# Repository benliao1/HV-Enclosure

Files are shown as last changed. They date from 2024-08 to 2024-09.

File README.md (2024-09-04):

# High Voltage Enclosure

This git repository contains all of the design files (both mechanical and electrical) as well as extensive documentation for the high voltage safety enclosure. It is meant to be living and not used simply as a reference. Any updates to the design should be uploaded to the repository, along with any necessary updates to the documentation files. Keeping these files up-to-date is important, especially since new high voltage enclosures or maintenance / part replacement on existing enclosures may require the files to be used again at any given time (unlike former research projects, which will be used as references but more likely than not will never be built again).

Note: **Do NOT** make a new commit to this repository while Solidworks is open!! Solidworks creates a bunch of temporary journal files and mod files while it is open which should not be committed to the repository.

## Overview

The high voltage safety enclosure is an assembly designed to protect someone in the event of a catastrophic mechanical failure of a converter under test or improper use of electrical equipment during a test which would otherwise result in the possibility of the person touching something at high voltage. The enclosure consists of the following parts:

- A **cover** which can be lowered to cover a portion of the lab bench and raised to allow access to the test setup
- A **latching mechanism** which holds the cover in the raised position
- A **button assembly** which detects when the cover is open or closed and which drives the electrical components of the enclosure
- An **HV Electrical Box** which contains electronics to operate the high voltage contactors and bleeder resistors on the input side of the converter under test
- An **Auxiliary HV Electrical Box** which is an __optional__ assembly containing electronics to operate bleeder resistors on the output side of the converter under test

The cover protects a person against catastrophic mechanical failure and against unintentional contact between a foreign object and the converter under test. The electrical boxes and button assembly ensure that the converter under test can only be energized (i.e. connected to the power supply) when the cover is down; when the cover is up, bleeder resistors are automatically connected across the input to bleed any large input capacitors that may be energized (and, if the auxiliary HV Electrical Box is used, bleeder resistors are automatically connected across the output to bleed any large output capacitors as well).

## Repository Structure

The following is a guide to where various files and components are located in this repository.

- The **mechanical** folder contains all of the CAD models of nearly every component used in the mechanical portion of the HV enclosure. Since the enclosure was designed in Solidworks, all CAD files are `.sldprt`, `.sldasm`, or `.step` files. Notably, this folder does **not include** any bolts, nuts, or L brackets used in the cover, and does **not include** the gate latch used in the latching mechanism. Below is a list of the kinds of files that can be found here:
	- All 8020 beams used in the cover and electrical boxes
	- All acrylic pieces used in the cover and electrical boxes
	- 3D exported renderings of the various PCBs in the design
- The **electrical** folder contains all of the Altium component libraries, schematics, and layouts for the various PCBs designed for the HV enclosure. Below is a list of the PCBs used in the design:
	- **Main Board**: this board connects to the incoming 12 V DC supply from the wall, sends power to the other boards, operates the contactors, sends signals to operate the bleeder resistors, receives the signal from the button detecting when the cover is closed or not, and displays the state of the system to the user.
	- **HV Board**: this board connects the power supply and the converter under test. It contains the high-voltage JFETs that connect/disconnect the bleeder resistors across the input of the converter, as well as mounting holes for the contactors which electrically connect/disconnet the power supply from the converter under test.
	- **Auxiliary HV Board**: this board connects the converter under test with the load. It contains high-voltage JFETs that connect/disconnect the bleeder resistors across the output of the converter.
	- **Button Board**: this board houses the lever switch which detects when the cover is closed, which is sent to the Main Board.
- The **production** folder contains all of the files that will be uploaded to various supplier websites for custom fabrication:
	- The `.STL` file of the button board holder model
	- The `.DXF` files for all of the acrylic panels
	- The `.DXF` files for all of the aluminum heat sinks
	- The `.ZIP` files containing the gerbers for all of the PCBs
- The **docs** folder contains more documentation and useful reference material:
	- BOMs for the mechanical and electrical components used in the HV enclosure (as well as the suppliers and supplier links of those components)
	- What supplier manufacturing options were selected when ordering the parts for the HV enclosure
	- Assembly instructions for the HV enclosure
	- Documents describing what needed to be considered and what principles were followed throughout the design process
	- All photos and screenshots used in the repository

## Quick Specifications

The following is a list of the most important specifications of the system as designed in the first prototype:

- Rated voltage: 1000 V
- Rated current (banana plugs): 25 A per plug
- Rated current (Phoenix connector): 75 A per pin
- Bleeder resistor value: 4x 390 Ohms in parallel (total 97.5 Ohms)
- Bleeder resistor power ratings: 100 W per resistor (continuous, with heat sink); 12.5x overload for 2 seconds
	- Maximum power dissipation is 5 kW for 2 seconds across entire resistor bank - appoximately enough to discharge 10 mF of input capacitance at 1000 V, reducing the voltage on the input bus below 100 V in a little over 2 seconds (see [datasheet](https://www.te.com/commerce/DocumentDelivery/DDEController?Action=srchrtrv&DocNm=1773035&DocType=DS&DocLang=English), page 3 "Power Overload" graph for details)

## Credits

First prototype designed and assembled by Ben Liao in late 2023 to mid 2024 (completed August 2024). Contributors to this first iteration included Logan Horowitz, Nathan Biesterfeld, Nathan Miles Ellis, and Robert Pilawa. Original documentation written by Ben Liao.

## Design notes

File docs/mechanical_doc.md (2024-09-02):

# Mechanical Design Documentation

This document contains information on the design process for the mechanical portion of the enclosure, notes on working on and editing the files/design, and the parameters that can be changed (for example, to make the box wider or narrower).

## Structure of `mechanical` Folder

To access the assembly, it is recommended to start by opening the `mechanical/full_model.SLDASM` file. Right clicking on indivisual components and selecting "Open Part" or "Open Subassembly" allows you to open additional components in the assembly. If you want to open individual components directly, the structure of the `mechanical` folder is as follows:

- `mechanical`: root directory
	- `full_model.SLDASM`: complete model of the enclosure along with desk and instruments for comparison. The cover can be moved up and down in this model by clicking and dragging it up and down.
	- `desk_and_instrument_models`: models of the desk, shelves, large DC power supply, large electronic load, and typical oscilloscope used in the full model.
	- `subassemblies`: various subassembly files that together make up the full model. This includes the cover and the electronics (which itself is made up of multiple subassemblies)
	- `parts`: all of the `.SLDPRT` files that makes up the enclosure.
		- `2020`: Solidworks part models of 20 series aluminum profile beams from [8020.net](8020.net) of various sizes, along with a drawing of the cross section and a base model (which can be copied and modified to create additional beam lengths should they be needed).
		- `acrylic`: Solidworks part models of all the acrylic pieces used in the cover and both the HV Electrical Box and the Auxiliary HV Electrical Box.
		- `bleed_resistor_parts`: Solidworks part models of the various components used to hold the bleed resistors and their aluminum heat sinks to the electrical boxes. This includes the nylon spacers and large L brackets.
		- `contactor_parts`: Solidworks part models of the contactor and the electrical connector used to operate the contactor coil
		- `miscellaneous`: Solidworks part models of miscellaneous components mainly used to connect other components together:
			- Standoffs for holding the PCBs inside the high voltage electrical boxes
			- The handle on the cover
			- The bar attached to the cover which engages with the gate latch on the top shelf (the gate latch is not modeled here, only the bar)
			- The 3D-printed holder for the button board which allows the button board to be precisely placed to detect when the cover is closed

## Design Considerations

This section describes the functional considerations that were taken into account throughout the design process.

- **Weight**: the cover and high voltage electrical boxes cannot be too heavy, since that would put undue stress on the mounting screws attached to the hinge attachment assemblies, especially when the cover is in the raised position
- **Cost**: highly specialized parts were mostly avoided, and the amount of structural material kept to a minimum in an effort to reduce cost
- **Ease of Use**: Spaces were left between the top of the cover and the front of the first shelf above the lab bench, as well as between the side panels of the cover and the lab bench, so that the user can route oscilloscope probes and control wires easily. The high voltage electrical boxes were also fitted with a simple connection to the 120 V AC grid for power, which eliminates the need for attaching a separate power supply to the enclosure.
- **Stability**: The cover is designed to be stable in the raised position; i.e. the cover will stay in the raised position by resting against the top shelf. The gate latch is not needed to keep it in the top position, but for greater safety and insurance that the cover won't fall down unexpetedly, it's still advised to latch the cover whenever it is in the raised position
- **Electrical Insulation**: Since there will be high voltage and current flowing through the high voltage electrical boxes, is is undesirable to openly expose the conducting surfaces of the high voltage boards and bleed resistors. The electrical boxes were designed to enclose the high voltage boards on five sides (with the underside of the first shelf forming the sixth side), protecting them from foreign objects as well as confining the high voltage to that small volume. In the event that a wire inside the box somehow breaks loose, the wire will not touch a piece of metal and energize the cover itself (unless it accidentally touches the tips of one of the bolts holding the acrylic to the metal box structure).

## Creating New 20 Series Profile Lengths

To makes a new 20 series beam length in Solidworks, go to `mechanical/parts/2020` and open `2020_base.SLDPRT`. Click on the Boss Extrude feature and edit the extrusion length as desired. Save the edited part as a new file and name it following the naming convention: `2020_<length>` where the length is in cm. For example, `2020_100` is 100 cm long. Lengths with decimals have dashes in replace of the period, e.g. `2020_25-4` for a beam 25.4 cm long.

## Nylon Spacers

Nylon spacers were used to separate the heat sinks and the acrylic panels because nylon has a higher melting temperature than acrylic and also resists thermal deformation below the melting temperature. Thus, in the event the bleed resistors and their heat sinks get extremely hot in an extreme use case, the nylon spacers will hopefully prevent the heat sinks from heating up the acrylic panels so much that they deform or otherwise cause structural damage to the high voltage electrical boxes.

## Allowable Dimension Adjustments

The height of the enclosure cannot be easily changed as the angle the cover makes with the lab bench is set; changing the height of the enclosure (i.e. the distance between the first shelf and the lab bench) would require changes to both the height and width of the cover as well as the non-right angle in the acrylic cover side panel.

### Enclosure Width

To change the width of the enclosure, the following items need to be edited:

- The length of the 20 series beams at the top and bottom of the cover
- The width of the acrylic top panel of the cover
- The length of the 20 series beam holding up the high voltage electrical boxes

All of these should be modified by the same length.

### Length Enclosure Extends Underneath First Shelf

If the supports for the enclosure interfere with the placement of lights underneath the first shelf, the following can be shortened to make room:

- The length of the 20 series beam in the hinge assemblies holding the enclosure to the bottom of the shelf

It is probably best to leave this beam to be as long as possible, as a longer beam provides better support. To make this distance even shorter, it may be necessary to modify the dimensions of the high voltage electrical boxes or turn them 90 degrees to mount them lengthwise along the aluminum bar.

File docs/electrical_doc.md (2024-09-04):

# Electrical Design Documentation

This document contains information on the design process for the electrical portion of the enclosure, notes on working on and editing the files/design, and the parameters that can be changed.

**It should be noted that much of the electronics is actually explained in the Altium schematics. Please read those for very detailed explanations of how the electrical circuitry actually works.** Thus, there will not be any documentation in this document explaining how the boards works.

## Structure of `electrical` Folder

The structure of this folder should be relatively self-exlanatory. Each of the four PCBs has its own Altium PCB Project, containing a schematic file, a layout file, and (with the exception of the Button Board) a populated smart BOM file for convenience. The two integrated libraries `HV_Box_IntLib.IntLib` and `Load_Bank_New_IntLib.IntLib` need to both be installed into your Altium workspace to properly open the files. Apologies for the fact that there's two integrated libraries -- I (Ben) didn't really know how they worked when I started this project so I used both a new integrated library created just for this project as well as components from a previous project I did.

## Schematic Rules and Net Classes

The schematics were made very carefully with a mind towards ease of understanding, good organization, and self-documentation. Generally, logic and power flow from left to right, top to bottom. Each section is demarcated with thick dark red boxes, and with a comment explaining the purpose and various quirks (if any) of that particular section.

Since all the PCBs (except the Button Board) have sections which handle different power regimes that require different clearances in the layout, each net on the boards is assigned a net class:

- "Low Voltage": this net class contains all logic signals and power rails that are referenced to the ground of the 120V-12V AC/DC converter plugged into the wall. The maximum voltage on any of these traces is 12 V.
- "Isolated": this net class contains all logic signals and power rails that have passed through either isolated gate drivers or the isolated power converts, but **do not** directly handle the high voltages and currents associated with the converter under test. The ground reference of these traces is the `JFET_SOURCE` net, i.e. the voltage attached to the source of the JFETs which connect/disconnect the bleeder resistors. The maximum voltage of any of these traces relative to that reference is 12 V, but the isolation barrier can see up to the voltage rating of the enclosure (1 kV), requiring large clearances between this net class and the Low Voltage net class.
- "High Voltage": this net class contains all of the mounting points, copper pours, and jacks which handle the high voltage and current associated with the converter under test. Every net in this net class can see a voltage difference of up to the voltage rating of the enclosure with every other net in the class, so all nets in this class requires large clearances with other members of the High Voltage class, as well as all members of the Isolated and Low Voltage classes

The three net classes are also assigned colors to make them easy to identify in both the schematic and the layout:

- "Low Voltage" class nets and blankets are colored yellow yellow
- "Isolated" class nets and blankets are colored blue blue
- "High Voltage" class nets and blankets are colored red red

## Connecting to the HV Board/Aux HV Board Phoenix Connectors

The Phoenix connectors that will connect to the ones used on the HV Board and Aux HV Board is the one at [this Digikey link](https://www.digikey.com/en/products/detail/phoenix-contact/1969373/2526720).

## Connecting Additional Current

The current rating of the contactors is 150 A. The banana blugs are rated for 25 A each, and the Phoenix connector is rated for 76 A. Here are the different ways to connect to the board for different current regimes:

- 0 A - 25 A: One set of banana plugs OR the Phoenix connector
- 25 A - 50 A: Both sets of banana blugs OR the Phoenix connector
- 50 A - 76 A: Phoenix connector
- 76 A - 101 A: One set of banana plugs AND the Phoenix connector
- 101 A - 126 A: Both sets of banana plugs AND the Phoenix connector
- 126 A - 150 A: Both sets of banana plugs AND the Phoenix connector AND a thick wire screwed directly to the M6 bolt connected to the contactor terminals

For current greater than 150 A, you will need to replace the contactor with one that can break higher current. Luckily, the manufacturer of the contactor used in the prototype makes contactors with higher rated currents in the same form factor, so that should be a quick swap-in if desired. However, the PCBs were only designed to handle 150 A, so pushing the PCBs past 150 A could result in some overheating in the copper pours.

## Contactors vs. Solid State Breakers

When designing the enclosure, there was a long discussion about whether to use contactors or solid state breakers to break the current between the supply and the converter under test. Solid state breakers are, in theory, better than contactors since they can turn on and off much faster and are cheaper / less bulky than contactors. But, in reality, there are no solid state breakers than can simultaneously block 1 kV and pass 150 A of current; you can only get one or the other. As such, there would need to be two different versions of the enclosure: one for high voltage, low current; and another for low(er) voltage, high current. This has the potential to cause a lot of confusion for the user. Additionally, the on-state resistance of solid-state breakers is typically greater than contactors, and at sufficiently high currents, would need heat sinks and a cooling apparatus to maintain safe operation. These would add a lot of bulk to the high voltage electrical box (comparable to the contactor) and a lot of additional complexity. The final reason that contactors were chosen over solid state breakers was that there was a concern that the contactors would wear out quickly because contactors have a relatively low life if they are constantly breaking high current (i.e. turning off at high current). This is true, but the only time that the contactors in the high voltage enclosure need to turn off at high current is if the user lifts the cover while a test is running (and thus, current is flowing through the contactor from the supply to the converter under test). Presumably, this should happen exceedingly rarely; under normal operation, the contactor stays closed for the entire duration that the system is energized. Thus, the relatively low life of the contactors when subjected to repeated high-curent breaks is of little concern to us.

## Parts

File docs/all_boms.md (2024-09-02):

# All BOMs

This document contains Bills of Materials for the entire enclosure, organized in two different ways. The first section is a list of components needed to build each section of the enclosure (PCBs, Cover, High Voltage Electrical Box, Auxiliary High Voltage Electrical Box, Wiring). The second section is all of the components needed to build the entire enclosure organized by supplier (JLCPCB, OSH Stencil, Digikey, 8020.net, Xometry, Sendcutsend, McMaster-Carr, a home improvement or electronics store, and Amazon).

# Section One (By Enclosure Section)

## PCBs

These BOMs contain the components needed to build **one** of the specified PCB with no attachments. They are duplicated in the Altium Smart BOMs. They do not include components that are not modeled in Altium, such as the contactors, bleeder resistors, and JST connector wires. See the BOMs for the [High Voltage Electrical Box and Auxiliary High Voltage Electrical Box](#electrical_box_boms) for those line entries.

### Button Board

| Part Name              | Quantity | Digikey Link                                                                                       |
|------------------------|----------|----------------------------------------------------------------------------------------------------|
| JST 3-pin connector    | 1        | [here](https://www.digikey.com/en/products/detail/jst-sales-america-inc/B3B-PH-SM4-TB/926642)      |
| Res. 100k 0.5%         | 1        | [here](https://www.digikey.com/en/products/detail/yageo/RC0603DR-07100KL/5917788)                  |
| Lever switch           | 1        | [here](https://www.digikey.com/en/products/detail/omron-electronics-inc-emc-div/D2FS-FL-N/4753388) |

### Main Board

| Part Name                        | Quantity | Digikey Link                                                                                                                                                                                                                                                                                                                                                                                                              |
|----------------------------------|----------|---------------------------------------------------------------------------------------------------------------------------------------------------------------------------------------------------------------------------------------------------------------------------------------------------------------------------------------------------------------------------------------------------------------------------|
| JST 2-pin connector              | 2        | [here](https://www.digikey.com/en/products/detail/jst-sales-america-inc/B2B-PH-SM4-TB/926641)                                                                                                                                                                                                                                                                                                                             |
| JST 3-pin connector              | 3        | [here](https://www.digikey.com/en/products/detail/jst-sales-america-inc/B3B-PH-SM4-TB/926642)                                                                                                                                                                                                                                                                                                                             |
| Phoenix connector 2x1 small      | 2        | [here](https://www.digikey.com/en/products/detail/phoenix-contact/1990009/950922)                                                                                                                                                                                                                                                                                                                                         |
| 12 V barrel jack                 | 1        | [here](https://www.digikey.com/en/products/detail/adam-tech/ADC-H-010-1/9831182)                                                                                                                                                                                                                                                                                                                                          |
| Contactor drive circuit NFET     | 1        | [here](https://www.digikey.com/en/products/detail/good-ark-semiconductor/GSFH9R015/22531590)                                                                                                                                                                                                                                                                                                                              |
| Logic NFET                       | 2        | [here](https://www.digikey.com/en/products/detail/good-ark-semiconductor/2N7002K/18667796)                                                                                                                                                                                                                                                                                                                                |
| IC single NOT gate               | 1        | [here](https://www.digikey.com/en/products/detail/texas-instruments/SN74AHC1G14DBVR/276736)                                                                                                                                                                                                                                                                                                                               |
| IC comparator                    | 1        | [here](https://www.digikey.com/en/products/detail/microchip-technology/MCP6541T-I-LT/551750)                                                                                                                                                                                                                                                                                                                              |
| IC isolated gate driver          | 1        | [here](https://www.digikey.com/en/products/detail/texas-instruments/UCC5350SBD/7899478?s=N4IgjCBcoGwJxVAYygMwIYBsDOBTANCAPZQDaIALAAxwDMdIAuoQA4AuUIAymwE4CWAOwDmIAL6EArAHYqiECkgYcBYmRC0ATDAqS5zEO048BI8YTBwAHAmgK0WPIRKRy%2BiSE01a8xcqdqruBMrByQIACSgmy4wri85p60VhS%2BDirO6l6a0lY%2BBkbhJkKiHgC0mmmQfACuqi7kkkzlMFW19er55RB2fo4dQZpwrYxiHpVB-NhEmOgxACYABMJzuIvzAgBu8SEgTXYsUGCsh5Cakh6tdvzznGVgVBChnCCEbACeLLic6NgoY0A) |
| IC level shifter x6              | 2        | [here](https://www.digikey.com/en/products/detail/onsemi/MC14504BDTR2G/1478864)                                                                                                                                                                                                                                                                                                                                           |
| Varistor                         | 2        | [here](https://www.digikey.com/en/products/detail/epcos-tdk-electronics/B72210S0300K101/651310?s=N4IgTCBcDaIAQCEDsYwEYAMBlDBmDGA0pmiALoC%2BQA)                                                                                                                                                                                                                                                                            |
| IC 3.3V fixed output LDO         | 1        | [here](https://www.digikey.com/en/products/detail/diodes-incorporated/AZ1117IH-3-3TRG1/5699672)                                                                                                                                                                                                                                                                                                                           |
| Red 0603 SMD LED                 | 4        | [here](https://www.digikey.com/en/products/detail/harvatek-corporation/B1911USD-20D000114U1930/15519991)                                                                                                                                                                                                                                                                                                                  |
| Blue 0603 SMD LED                | 2        | [here](https://www.digikey.com/en/products/detail/harvatek-corporation/B1931NB-20C007614U1930/15861263)                                                                                                                                                                                                                                                                                                                   |
| Cap. 10 uF, 25 V Al electrolytic | 3        | [here](https://www.digikey.com/en/products/detail/w%C3%BCrth-elektronik/865080440002/5728025)                                                                                                                                                                                                                                                                                                                             |
| Cap. 22 uF, 25 V 1206            | 1        | [here](https://www.digikey.com/en/products/detail/samsung-electro-mechanics/CL31A226KAHNNNE/3888705)                                                                                                                                                                                                                                                                                                                      |
| Cap. 470 nF, 50 V C0G/NP0        | 2        | [here](https://www.digikey.com/en/products/detail/murata-electronics/GRM31C5C1E474JE01L/16033870)                                                                                                                                                                                                                                                                                                                         |
| Cap. 47 nF, 25 V C0G/NP0         | 1        | [here](https://www.digikey.com/en/products/detail/kemet/C0805C473J3GAC7800/2212853)                                                                                                                                                                                                                                                                                                                                       |
| Cap. 1 uF, 50 V                  | 6        | [here](https://www.digikey.com/en/products/detail/samsung-electro-mechanics/CL10A105KB8NNNC/3887518)                                                                                                                                                                                                                                                                                                                      |
| Cap. 10 uF, 50 V                 | 2        | [here](https://www.digikey.com/en/products/detail/murata-electronics/GRM21BR61H106KE43K/15191954)                                                                                                                                                                                                                                                                                                                         |
| Cap. 100 nF 25 V                 | 1        | [here](https://www.digikey.com/en/products/detail/kyocera-avx/KGM15BR71E104KM/3247517)                                                                                                                                                                                                                                                                                                                                    |
| Res. 51 1%                       | 2        | [here](https://www.digikey.com/en/products/detail/yageo/RC0603FR-0751RL/727281)                                                                                                                                                                                                                                                                                                                                           |
| Res. 3.3k 1%                     | 5        | [here](https://www.digikey.com/en/products/detail/yageo/RC0603FR-103K3L/13694210)                                                                                                                                                                                                                                                                                                                                         |
| Res. 1k 0.1%                     | 1        | [here](https://www.digikey.com/en/products/detail/vishay-beyschlag-draloric-bc-components/MCT06030D1001BP100/2801070)                                                                                                                                                                                                                                                                                                     |
| Res. 3k 0.1%                     | 1        | [here](https://www.digikey.com/en/products/detail/panasonic-electronic-components/ERA-3AEB302V/1465865)                                                                                                                                                                                                                                                                                                                   |
| Res. 100k 0.5%                   | 1        | [here](https://www.digikey.com/en/products/detail/yageo/RC0603DR-07100KL/5917788)                                                                                                                                                                                                                                                                                                                                         |
| Res. 698 0.5%                    | 1        | [here](https://www.digikey.com/en/products/detail/yageo/RT0603DRE07698RL/1074957)                                                                                                                                                                                                                                                                                                                                         |
| Res. 0 jumper 2512               | 2        | [here](https://www.digikey.com/en/products/detail/bourns-inc/CR2512-J-000ELF/2345096)                                                                                                                                                                                                                                                                                                                                     |
| Res. 10k 1%                      | 1        | [here](https://www.digikey.com/en/products/detail/yageo/RC0603FR-0710KL/726880)                                                                                                                                                                                                                                                                                                                                           |

### HV Board and Aux HV Board

The BOMs for these two boards are the same.

| Part Name                           | Quantity | Digikey Link                                                                                                                                                                                                                                                                                                                                                                                                              |
|-------------------------------------|----------|---------------------------------------------------------------------------------------------------------------------------------------------------------------------------------------------------------------------------------------------------------------------------------------------------------------------------------------------------------------------------------------------------------------------------|
| Bleed resistor JFET                 | 2        | [here](https://www.digikey.com/en/products/detail/qorvo/UJ3N120065K3S/12617285)                                                                                                                                                                                                                                                                                                                                           |
| JST 3-pin connector                 | 1        | [here](https://www.digikey.com/en/products/detail/jst-sales-america-inc/B3B-PH-SM4-TB/926642)                                                                                                                                                                                                                                                                                                                             |
| JST 2-pin connector                 | 1        | [here](https://www.digikey.com/en/products/detail/jst-sales-america-inc/B2B-PH-SM4-TB/926641)                                                                                                                                                                                                                                                                                                                             |
| Banana plug, black                  | 4        | [here](https://www.digikey.com/en/products/detail/cal-test-electronics/CT3151SP-0/5267756)                                                                                                                                                                                                                                                                                                                                |
| Banana plug, red                    | 4        | [here](https://www.digikey.com/en/products/detail/cal-test-electronics/CT3151SP-2/6005547)                                                                                                                                                                                                                                                                                                                                |
| Phoenix connector, 2x1 large        | 2        | [here](https://www.digikey.com/en/products/detail/phoenix-contact/1969616/3605196)                                                                                                                                                                                                                                                                                                                                        |
| IC 12V-12V DC-DC isolated converter | 1        | [here](https://www.digikey.com/en/products/detail/xp-power/IV1212SA/4487989)                                                                                                                                                                                                                                                                                                                                              |
| IC isolated gate driver             | 1        | [here](https://www.digikey.com/en/products/detail/texas-instruments/UCC5350SBD/7899478?s=N4IgjCBcoGwJxVAYygMwIYBsDOBTANCAPZQDaIALAAxwDMdIAuoQA4AuUIAymwE4CWAOwDmIAL6EArAHYqiECkgYcBYmRC0ATDAqS5zEO048BI8YTBwAHAmgK0WPIRKRy%2BiSE01a8xcqdqruBMrByQIACSgmy4wri85p60VhS%2BDirO6l6a0lY%2BBkbhJkKiHgC0mmmQfACuqi7kkkzlMFW19er55RB2fo4dQZpwrYxiHpVB-NhEmOgxACYABMJzuIvzAgBu8SEgTXYsUGCsh5Cakh6tdvzznGVgVBChnCCEbACeLLic6NgoY0A) |
| Cap. 2.2 uF, 25 V                   | 2        | [here](https://www.digikey.com/en/products/detail/murata-electronics/GRM188R61E225KA12J/4905350)                                                                                                                                                                                                                                                                                                                          |
| Cap. 100 nF, 25 V                   | 1        | [here](https://www.digikey.com/en/products/detail/kyocera-avx/KGM15BR71E104KM/3247517)                                                                                                                                                                                                                                                                                                                                    |
| Cap. 10 uF, 50 V                    | 1        | [here](https://www.digikey.com/en/products/detail/murata-electronics/GRM21BR61H106KE43K/15191954)                                                                                                                                                                                                                                                                                                                         |
| Cap. 47 nF, 25 V C0G/NP0            | 1        | [here](https://www.digikey.com/en/products/detail/kemet/C0805C473J3GAC7800/2212853)                                                                                                                                                                                                                                                                                                                                       |
| Res. 3.3k 1%                        | 1        | [here](https://www.digikey.com/en/products/detail/kemet/C0805C473J3GAC7800/2212853)                                                                                                                                                                                                                                                                                                                                       |
| Res. 51 1%                          | 4        | [here](https://www.digikey.com/en/products/detail/yageo/RC0603FR-0751RL/727281)                                                                                                                                                                                                                                                                                                                                           |
| Res. 10k 1%                         | 1        | [here](https://www.digikey.com/en/products/detail/yageo/RC0603FR-0710KL/726880)                                                                                                                                                                                                                                                                                                                                           |

## Cover (Including Hinge Assembly and Gate Latch, and Button Board Hardware)

| Part Name                     | Quantity    | Supplier         | Supplier Link (if applicable)                                                                              |
|-------------------------------|-------------|------------------|------------------------------------------------------------------------------------------------------------|
| 100 cm 20 series beam         | 2           | 8020             | [here](https://8020.net/20-2020.html)                                                                      |
| 61.6 cm 20 series beam        | 2           | "                | "                                                                                                          |
| 6 cm 20 series beam           | 2           | "                | "                                                                                                          |
| 25.4 cm 20 series beam        | 2           | "                | "                                                                                                          |
| 90 cm 20 series beam          | 1           | "                | "                                                                                                          |
| 15 cm 20 series beam          | 1           | "                | "                                                                                                          |
| 20 series economy T nuts      | 59          | "                | [here](https://8020.net/14122.html)                                                                        |
| Button board holder           | 1           | Xometry          | N/A                                                                                                        |
| Acrylic cover top panel       | 1           | Sendcutsend      | N/A                                                                                                        |
| Acrylic cover side panel      | 2           | "                | N/A                                                                                                        |
| Gate latch                    | 1           | Amazon           | [here](https://www.amazon.com/dp/B09DBHG6NW)                                                               |
| 20 series hinge               | 1 pack      | "                | [here](https://www.amazon.com/LUORNG-Aluminum-Profile-Install-Extrusion/dp/B0B3J6YB91/ref=sr_1_62?sr=8-62) |
| 20 series L brackets          | 14 (1 pack) | "                | [here](https://www.amazon.com/dp/B0855V2JV3)                                                               |
| 20 series metal handle        | 1           | "                | [here](https://www.amazon.com/gp/product/B07NQ5WHW9/ref=ppx_yo_dt_b_asin_title_o00_s00?ie=UTF8&psc=1)      |
| M5-0.8 10mm flat head screw   | 8 (1 pack)  | McMaster-Carr    | [here](https://www.mcmaster.com/91263A832/)                                                                |
| M5-0.8 8mm button head screw  | 24 (1 pack) | "                | [here](https://www.mcmaster.com/92095A207/)                                                                |
| M5-0.8 10mm button head screw | 17 (1 pack) | "                | [here](https://www.mcmaster.com/92095A208/)                                                                |
| 3-56 5/16" pan head screw     | 2 (1 pack)  | "                | [here](https://www.mcmaster.com/91772A032/)                                                                |
| 3-56 hex nut                  | 2 (1 pack)  | "                | [here](https://www.mcmaster.com/90480A041/)                                                                |
| Button Board                  | 1           | JLCPCB, Digikey  | N/A                                                                                                        |
| Wood Screws                   | 4-5         | ex. ACE Hardware | N/A                                                                                                        |
| Wood 2x4 beam                 | 1           | "                | N/A                                                                                                        |

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

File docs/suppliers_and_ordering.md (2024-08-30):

# Suppliers and Ordering

This document lists where all of the components were ordered from and what options were chosen for those components (copper thickness of PCBs, 3D print material, etc.).

## PCBs

PCBs were ordered from JLCPCB. Options for the various boards are as follows:

- Main Board: 1 oz outer copper, 1/2 oz inner copper, HASL surface finish (leaded)
- HV Board: 2 oz outer copper, 2 oz inner copper, HASL surface finish (leaded)
- Aux HV Board: 2 oz outer copper, 2 oz inner copper, HASL surface finish (leaded)
- Button Board: 1 oz outer copper, HASL surface finish (leaded)

## PCB Stencils

Stencils were ordered from OSH Stencils. The HV Board and the Aux HV Board have the same stencil (this was intentional, to eliminate confusion between the two). Of course, the Button Board does not need a stencil. The options for the three stencils were as follows: 

- Stainless steel, 4mil thickness

## 3D Printed Button Holder

The button holder was ordered from Xometry, using the following options:

- Technology: Fused Deposition Modeling (FDM)
- Material: Protyping PLA (FFF)
- Color: next available (doesn't matter)
- Finish: Standard

## Acrylic

These were ordered from Sendcutsend. Options for these components were as follows:

- Material: Acrylic-Clear
- Thickness: 0.177"
- No post-processing options

## Aluminum Heat Sinks

These were ordered from Sendcutsend. Options for these components were as follows:

- Material: 6061 T6 Aluminum
- Thickness: 0.125"
- Post-processing options: Deburring

## 20 Series Beams and Fasteners

These were ordered from [8020.net](8020.net). See `all_boms.md` for full list of components ordered from this website.

## Screws, Nuts, Bolts, Aluminum L brackets for Heat Sinks

These were ordered from McMaster-Carr.

## 120 V - 12 V AC/DC Converter, Gate Latch, Cover Handle, Nylon Spacers

These were ordered from Amazon.

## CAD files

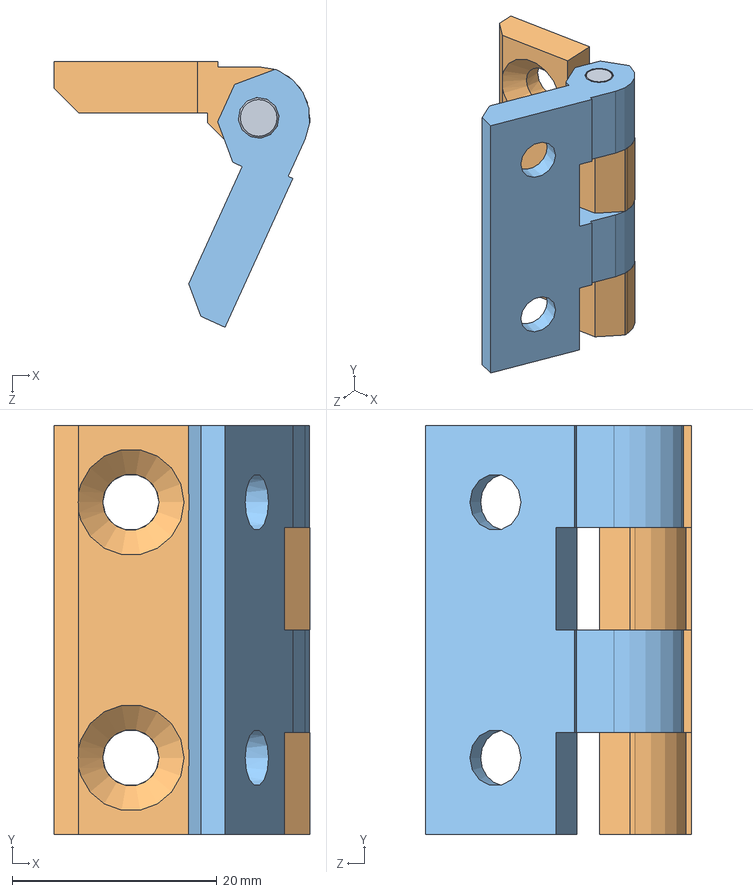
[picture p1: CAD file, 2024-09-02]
mechanical/parts/miscellaneous/hinge/hinge_assembly.sldasm
25.0 x 40.0 x 26.0 mm
hinge_pin
hinge_side_a
hinge_side_b

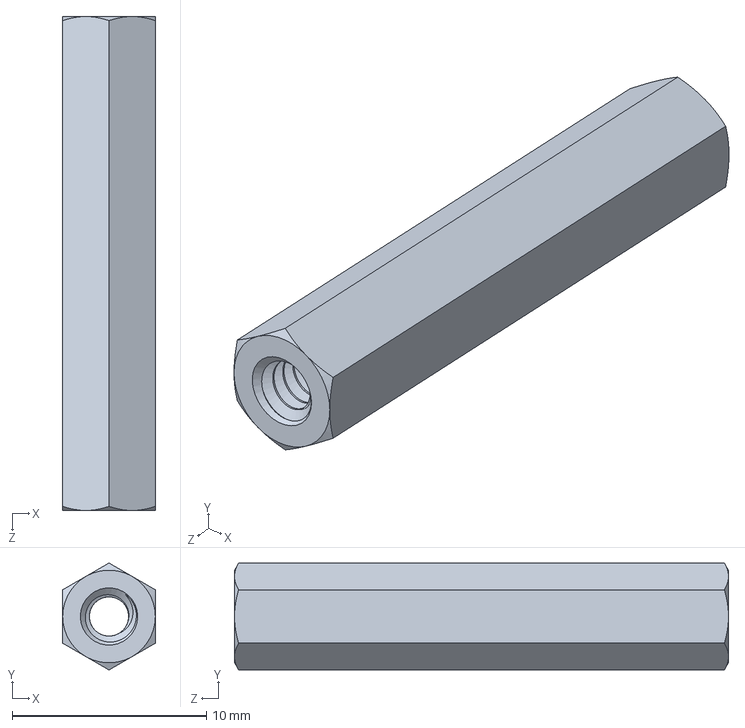
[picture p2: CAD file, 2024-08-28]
mechanical/parts/miscellaneous/standoff_main_board_1in_4-40.SLDPRT
4.76 x 5.50 x 25.4 mm

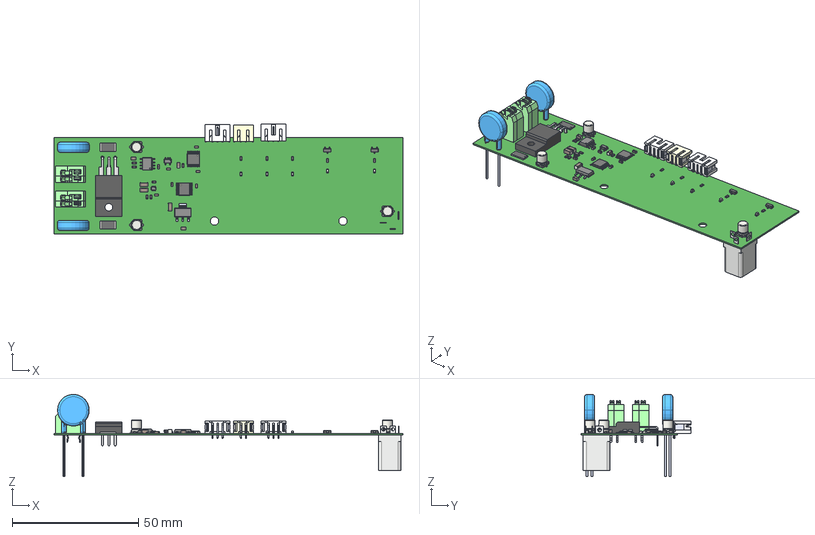
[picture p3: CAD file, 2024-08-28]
mechanical/parts/pcbs/main_board_pcb.step
138.0 x 43.4 x 32.5 mm
2512_res x 2
0603_cap x 7
level_shifter x 2
0603_res x 11
0805_cap x 3
alum_cap x 3
disc10 x 2
sc70_6pin
sot223-3
sot23_5pin
gate_driver
fet
3pin_jst x 2
barrel_jack
1206_cap x 3
0603_led x 5
nfet x 2
B2B-PH-SM4-TB_B2B-PH-SM4-TB

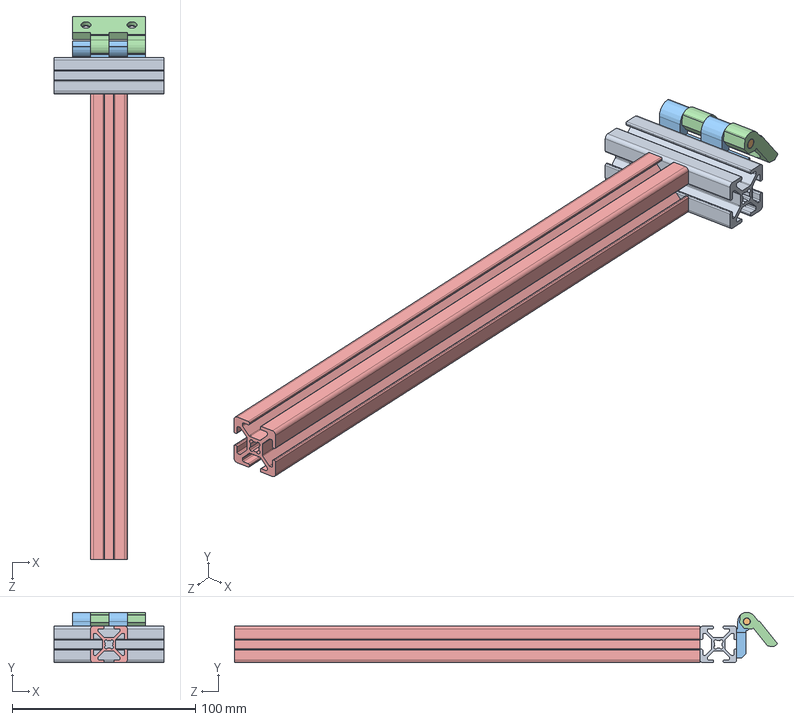
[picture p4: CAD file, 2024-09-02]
mechanical/subassemblies/cover_hinge_attachment.SLDASM
60.0 x 27.5 x 296.3 mm
hinge_pin
hinge_side_a
hinge_side_b

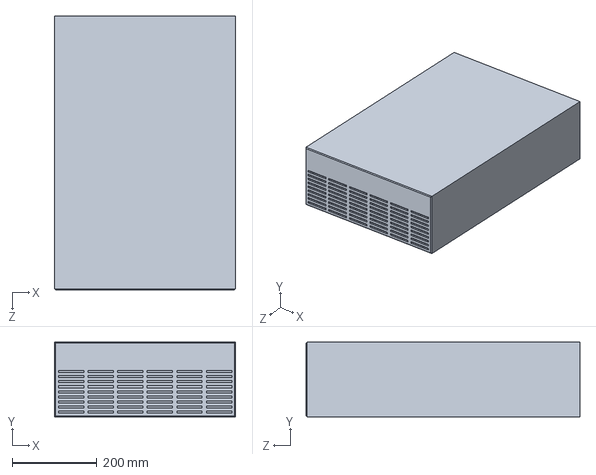
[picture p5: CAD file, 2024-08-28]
mechanical/desk_and_instrument_models/load_model.SLDPRT
428.0 x 177.0 x 647.0 mm

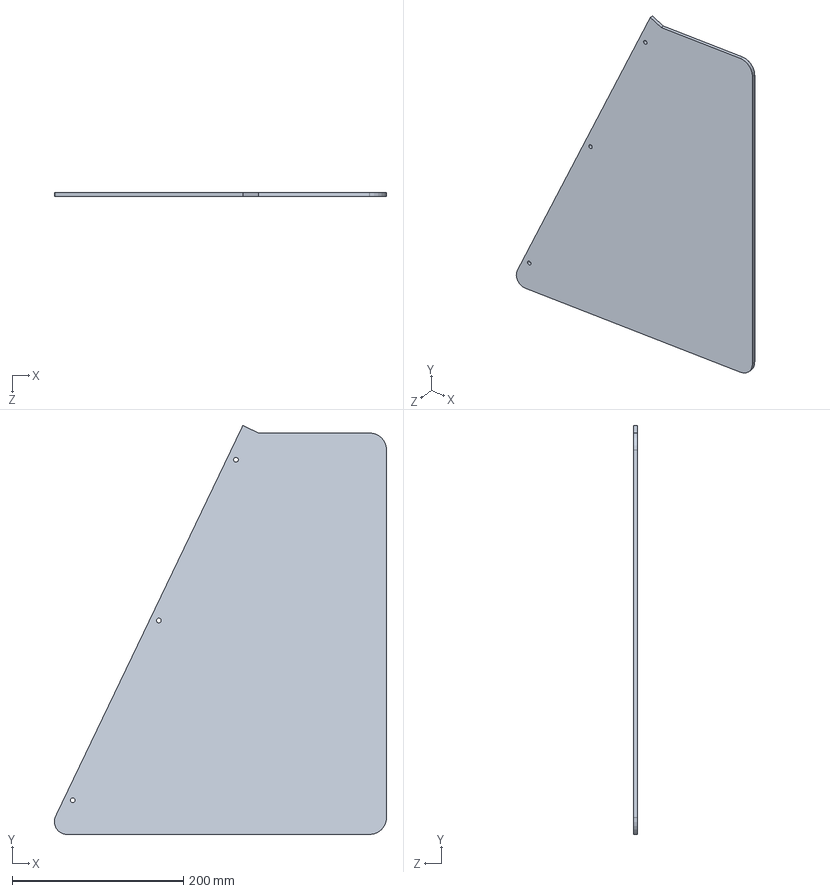
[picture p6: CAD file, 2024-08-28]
mechanical/parts/acrylic/cover_side_panel.SLDPRT
388.3 x 477.9 x 4.76 mm

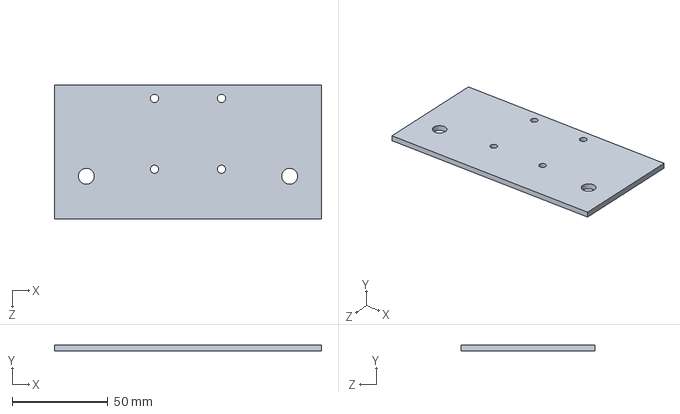
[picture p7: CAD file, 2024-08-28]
mechanical/parts/bleed_resistor_parts/hv_box_heat_sink_side.SLDPRT
139.7 x 3.17 x 69.8 mm

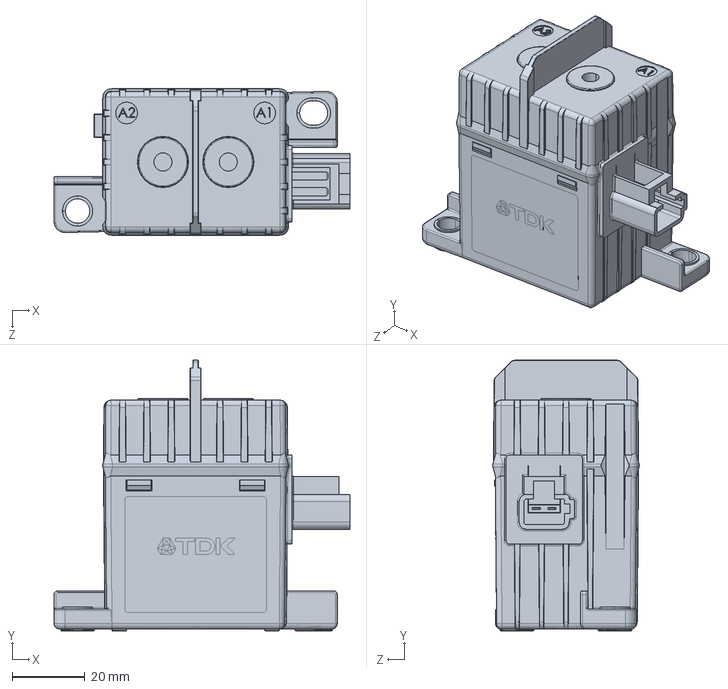
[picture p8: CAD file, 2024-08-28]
mechanical/parts/contactor_parts/contactor.SLDPRT
81.5 x 74.5 x 40.4 mm

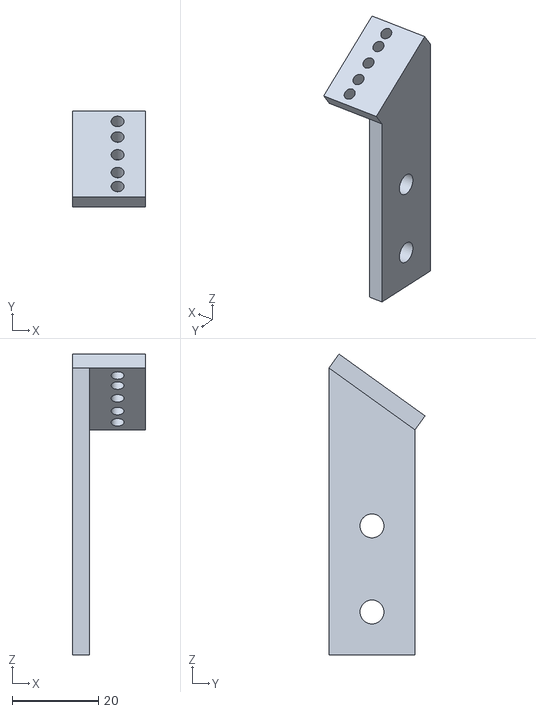
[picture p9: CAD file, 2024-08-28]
production/3d_print/button_board_holder.STL
17.0 x 22.3 x 69.9

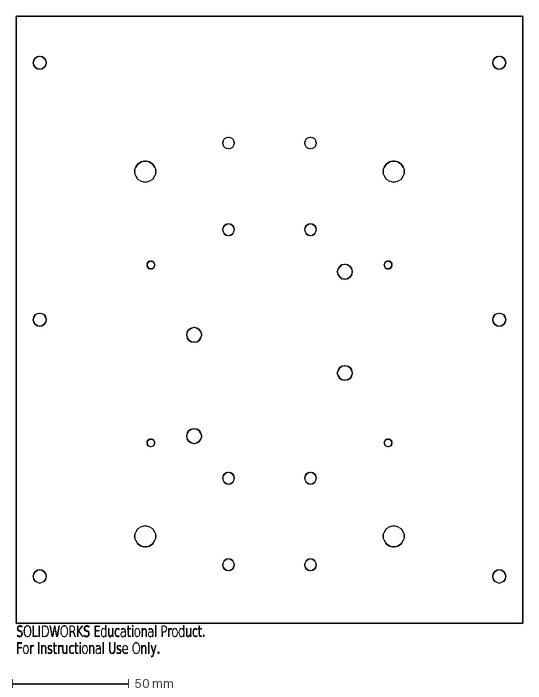
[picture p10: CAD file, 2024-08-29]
production/acrylic/hv_board_box_bottom_panel.DXF
SOLIDWORKS Educational Product.
For Instructional Use Only.

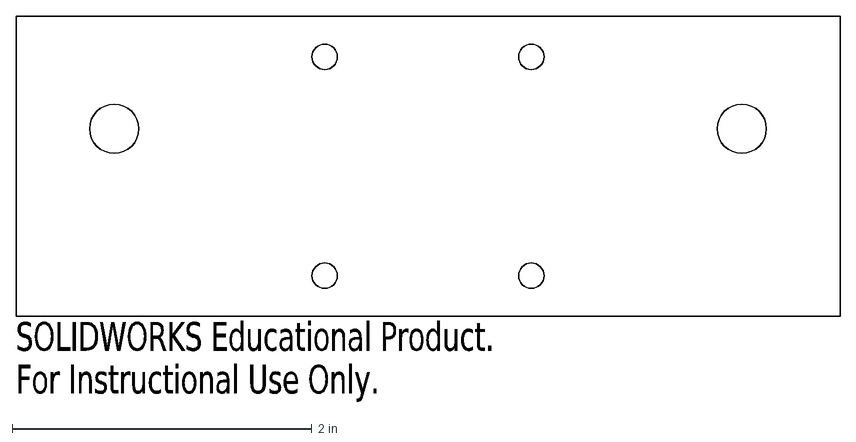
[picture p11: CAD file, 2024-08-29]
production/aluminum/heat_sink_bottom_resistor.DXF
SOLIDWORKS Educational Product.
For Instructional Use Only.

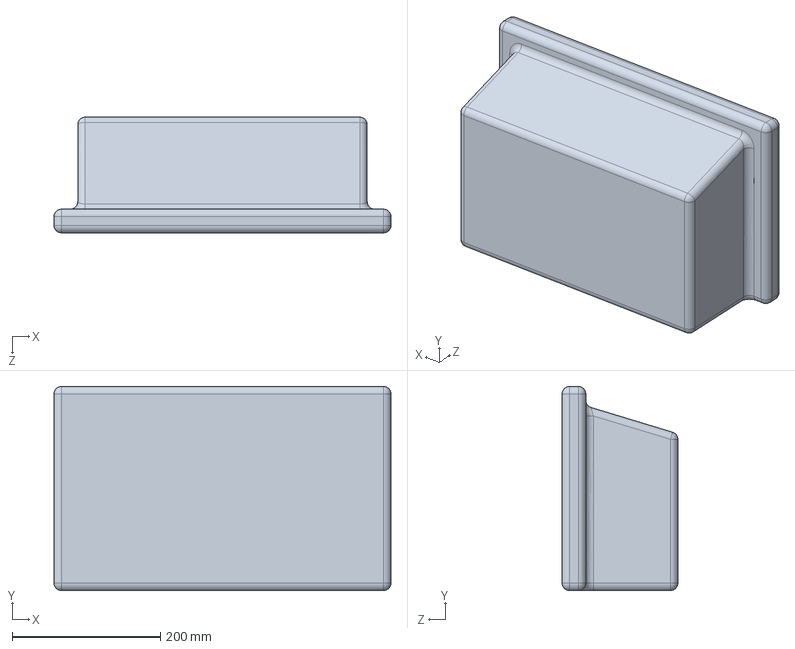
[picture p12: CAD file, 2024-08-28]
mechanical/desk_and_instrument_models/oscilloscope_model.SLDPRT
454.0 x 275.0 x 156.0 mm

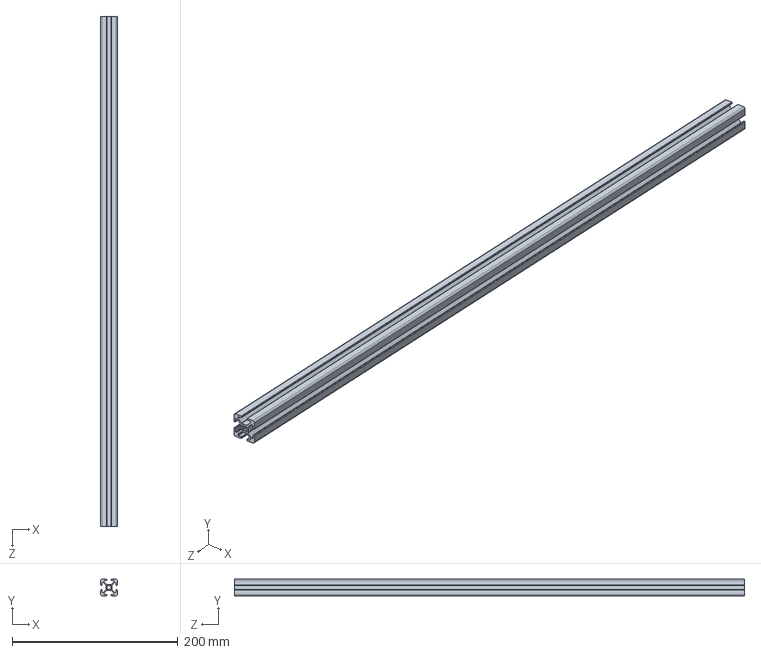
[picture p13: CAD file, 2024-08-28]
mechanical/parts/2020/2020_61-6.SLDPRT
20.0 x 20.0 x 616.0 mm

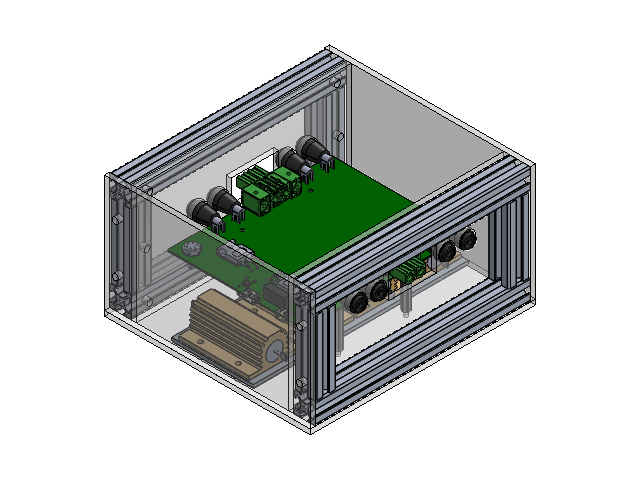
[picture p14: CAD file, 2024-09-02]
mechanical/subassemblies/aux_hv_pcb_assembly.SLDASM
aux_hv_board_pcb
chassis_resistor x 4
aux_hv_box_heat_sink
nylon_spacer_small x 16
standoff_aux_hv_board_2in_4-40 x 4
aux_hv_board_box_bottom_panel
aux_hv_board_box_side_panel x 2
aux_hv_board_box_front_back_panel x 2

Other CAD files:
mechanical/subassemblies/aux_hv_board_bleeder_resistor_assembly.SLDASM
mechanical/subassemblies/hv_board_bleeder_resistor_assembly_half.SLDASM
mechanical/subassemblies/cover.SLDASM
mechanical/parts/2020/cross_section.DWG
mechanical/desk_and_instrument_models/big_power_supply_model.SLDPRT
mechanical/desk_and_instrument_models/desk_and_shelf.SLDPRT
mechanical/parts/2020/2020_100.SLDPRT
mechanical/parts/2020/2020_15.SLDPRT
mechanical/parts/2020/2020_20.SLDPRT
mechanical/parts/2020/2020_25-4.SLDPRT
mechanical/parts/2020/2020_25.SLDPRT
mechanical/parts/2020/2020_6-9.SLDPRT
mechanical/parts/2020/2020_6.SLDPRT
mechanical/parts/2020/2020_9-4.SLDPRT
mechanical/parts/2020/2020_90.SLDPRT
mechanical/parts/2020/2020_base.SLDPRT
mechanical/parts/acrylic/aux_hv_board_box_bottom_panel.SLDPRT
mechanical/parts/acrylic/aux_hv_board_box_front_back_panel.SLDPRT
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

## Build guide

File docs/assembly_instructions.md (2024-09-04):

# Assembly Instructions

This document attempts to walk through the process of assembling the system with visuals. The hope is that this document can clarify any confusion there may be for where certain screws are placed, as well as offer some tips on how to assemble the structure.

## General Notes

- The economy T square nuts used for the 8020 pieces must be inserted before the channel that is cut into the 8020 profile that holds them in place is closed (i.e. they are not roll-in nuts). Before securing two 8020 profiles together, make sure all of the required T nuts have been placed in the profile. A small allen key is very useful for moving the T nuts within the profile so that they line up with holes in the acrylic or L brackets.
- M5-0.8 8mm screws are used to connect the L brackets with the 20 series beams.
- M5-0.8 10mm screws are used to connect the acrylic panels with the 20 series beams.
- **Do not** overtighten screws and nuts that hold acrylic to the 20 series beams. The acrylic will crack! The acrylic is not a structurally important part of the cover by design, so the bolts do not need to be overtightened. Tighten until snug and that should be fine.
- **Do** tighten the screws and nuts holding the L brackets to the 20 series beams. These are the most structurally important connections; tighten until snug and then give it another quarter-turn or so.

## Step 1: Building the PCBs

For the Main Board, use the reflow oven with normal settings, nothing too special here.

The HV Board and Aux HV Board have four layers of large and thick copper pours across the entire board, making it very difficult to solder. Make sure to reflow these boards for much longer than normal. Consider reflowing them with the banana plugs and Phoenix connectors on the board as well, since it is very difficult to solder them to the board when the board is cold.

The Button Board should be assembled by hand. Ensure that the lever switch is oriented in the correct direction (with the "hinge" of the lever closest to the JST connector) and flat against the PCB.

## Step 2: The Cover

Assemble the section shown in the image below, with annotations indicating the lengths of the 20 series beams (in red), the locations of the 4 L brackets (in blue), and the locations of the M5 bolts that are bolted into the cover top acrylic panel (in green). The purple arrows indicate the locations of the holes where the side panels are to be screwed in. The purple circle indicate the locations of 4 T nuts that need to inserted into the back of the top 100 cm beam which will accomodate the screws for the hinges in a later step.

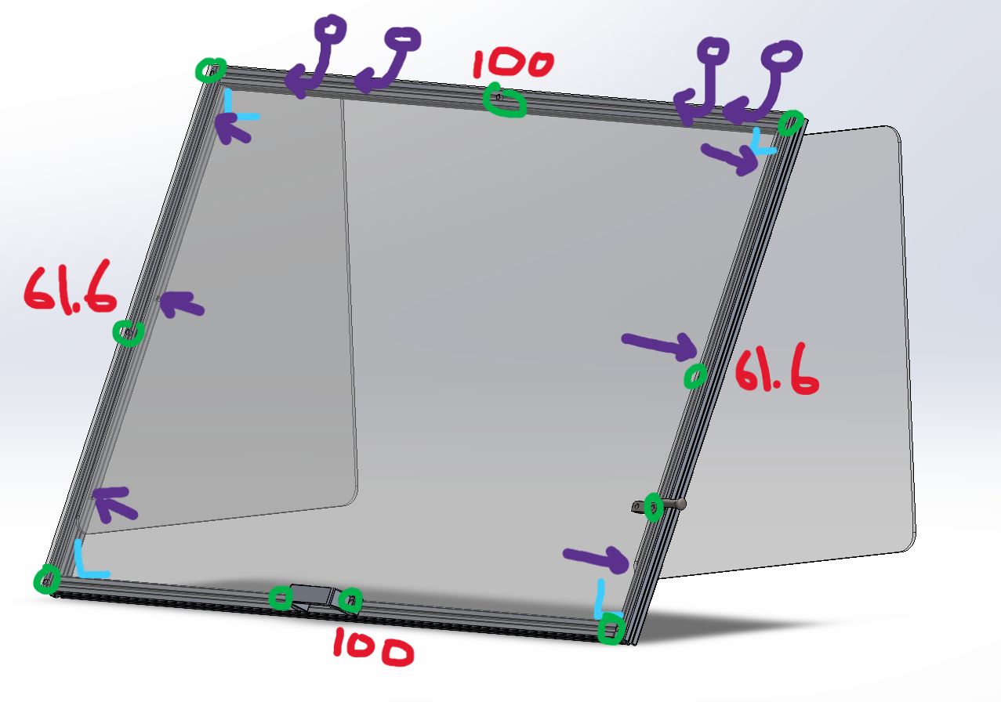
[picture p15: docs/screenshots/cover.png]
cover-diagram


Assemble the two hinge assemblies, connect them with the electronics support bar, and attach the button board assembly as shown in the annotated image below. The 3D-printed button board holder should be connected to the 15 cm beam with 10mm M5 bolts. Use the #3-56 bolts to secure the Button Board to the button board holder into the top and bottom holes of the button board holder (the three middle holes are for the 3 leads of the lever switch). The lengths of the beams are annotated on the diagram, along with the locations of the L brackets. The purple circles indicate the locations of T nuts for connection with the electrical boxes later; four on the front of the beam, and four on the back of the beam. Make sure that you use 4 M5-0.8 10mm **flat-head screws** to attach the hinges to the the 6 cm beams.

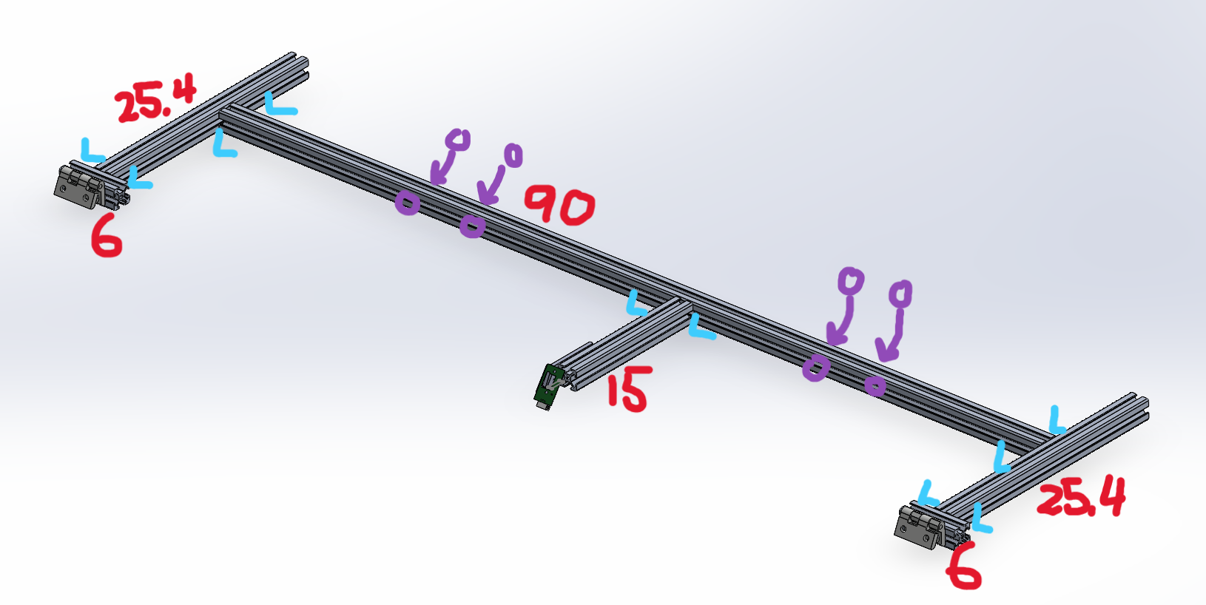
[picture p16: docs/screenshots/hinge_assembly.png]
hinge-assembly-diagram


Connect the hinge assembly to the cover with the remaining M5-0.8 10mm **flat-head screws**. Step 2 is complete when the assembly looks like the image below.

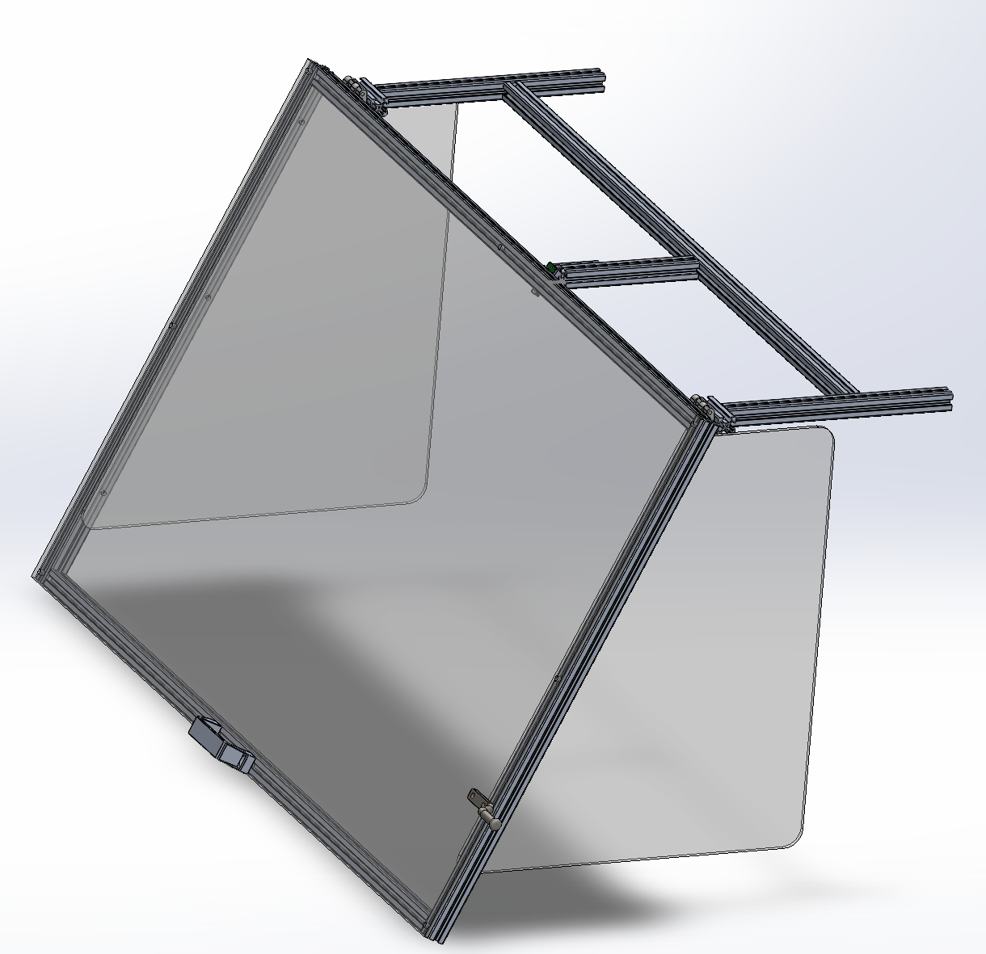
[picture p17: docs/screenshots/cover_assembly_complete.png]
cover-assembly-complete


## Step 3: The High Voltage Electrical Box

Assemble the two bleeder resistor assemblies. The Aluminum L brackets from McMaster come with screws and nuts; these can be used for the holes that point downwards, but the shorter 1/4"-20 screws bought separately from McMaster must be used for the holes that point horizontally. Similarly, the longer #8-32 screws should be used to attach the bottom resistors to their heat sinks, but the shorter 8-32 screws should be used to attach the side resistors to their heat sinks. This is annotated in the diagram below:

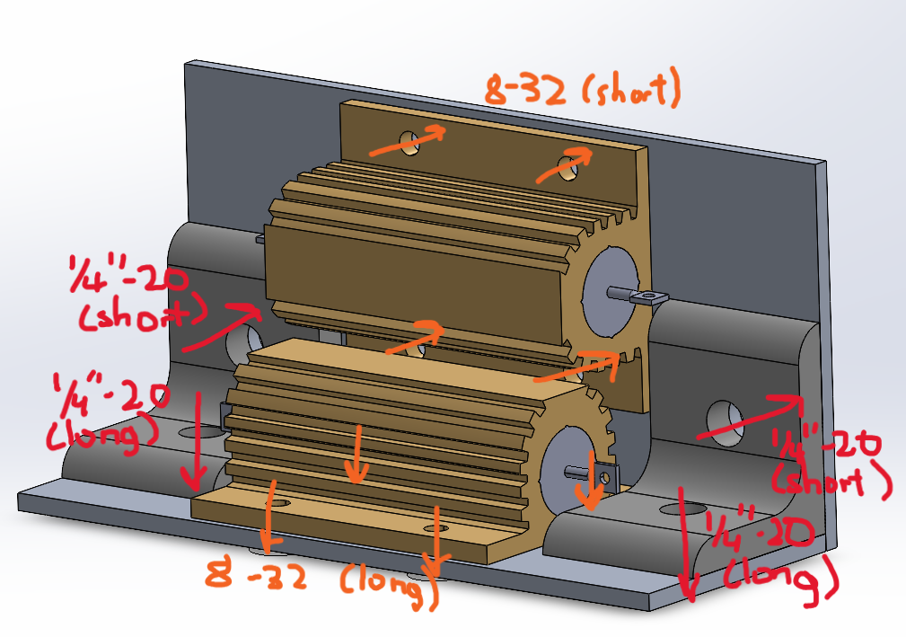
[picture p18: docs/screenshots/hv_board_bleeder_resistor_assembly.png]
hv-board-bleeder-resistor-assembly-diagram


Attach the bleeder resistor assemblies to the bottom acrylic panel. Ensure that there are nylon spacers between the bottom heat sink and the top of the acrylic panel, and another nylon spacer between the bottom of the acrylic panel and the nut on the end of the screw. Large nylon spacers are used for the 1/4"-20 screws; small nylon spacers are used for the #8-32 screws. When finished with this step, the box should look like this:

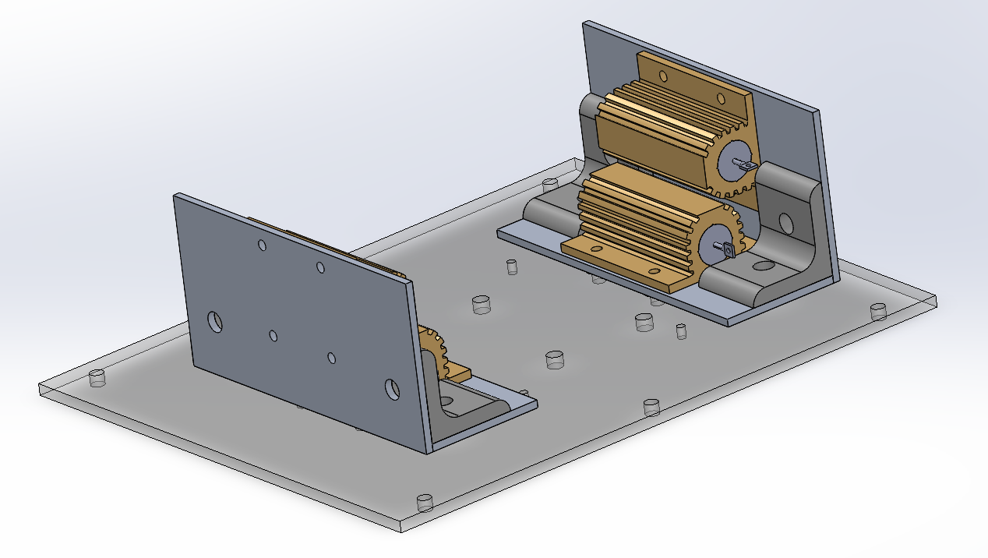
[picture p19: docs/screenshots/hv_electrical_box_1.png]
hv-electrical-box-1


Attach the contactors to the bottom acrylic panel. Use #8-32 screws (no nylon spacers necessary). Note the direction the contactors are placed (the port for the contactor connection accessory should be on the left side, looking from the front of the box). Leave some play in the screws so that the position of the contactors can be adjusted to fit the HV Board PCB. Attach the four #4-40 3" standoffs to the bottom panel as well with #4-40 screws. When finished with this step, the box should look like this:

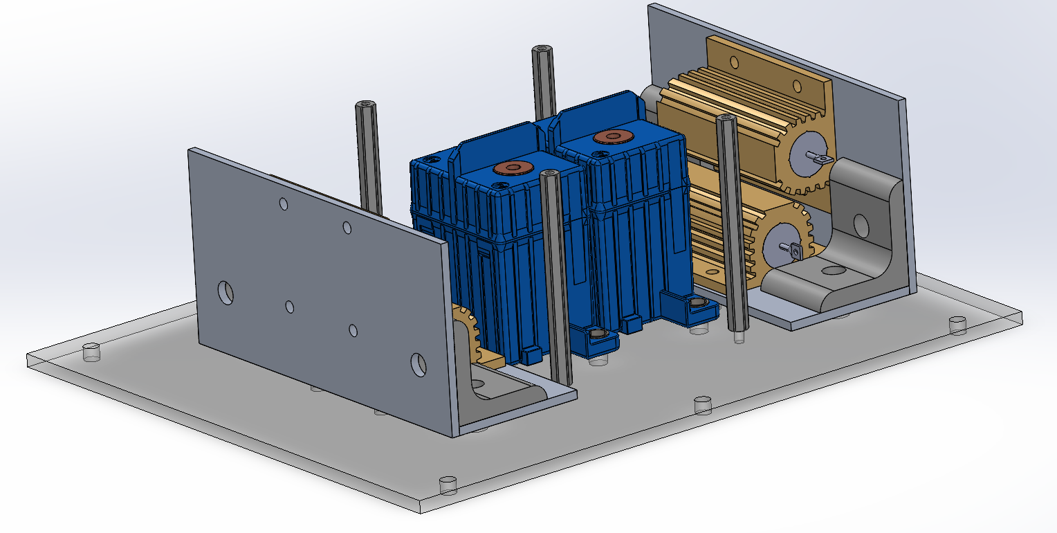
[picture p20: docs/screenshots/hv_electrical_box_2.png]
hv-electrical-box-2


Solder the wires connecting the bleeder resistors together on both sides, and that connect the bleed resistors up to the HV Board. These wires are 12 gauge. The wire that connects from the bleed resistor up to the HV board needs to have a ring terminal on one end big enough to accomodate an M6 bolt. The M6 bolt will be screwed through the hole in the HV Board PCB and secured in place by a nut. Afterwards, put the HV Board PCB on top of the four standoffs and secure it in place with #4-40 screws. Insert M6 bolts into the mounting locations for the contactors, screw on a nut onto each bolt, then screw the bolt into the threaded hole in the contactor. When the head of the bolt touches the top surface of HV Board PCB, stop turning the bolt into the contactor (as this would bend the PCB). To secure the bolt, turn the nut that you put on earlier counterclockwise when looking from above up towards the underside of the PCB. Tighten the nut. Finally, lock the contactors in place by tightening down the #8-32 screws holding them to the bottom acrylic panel. When finished with this step, the box should look something like the pictures below, with the wires drawn on as an example:

Right view:
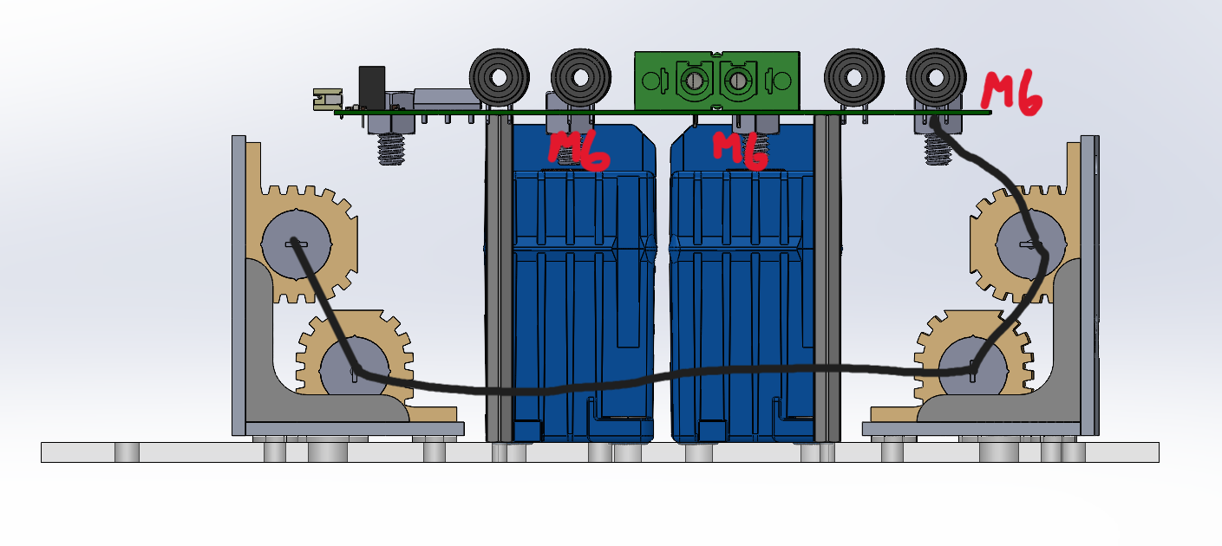
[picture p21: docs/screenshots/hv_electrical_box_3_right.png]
hv-electrical-box-3-right


Left view:
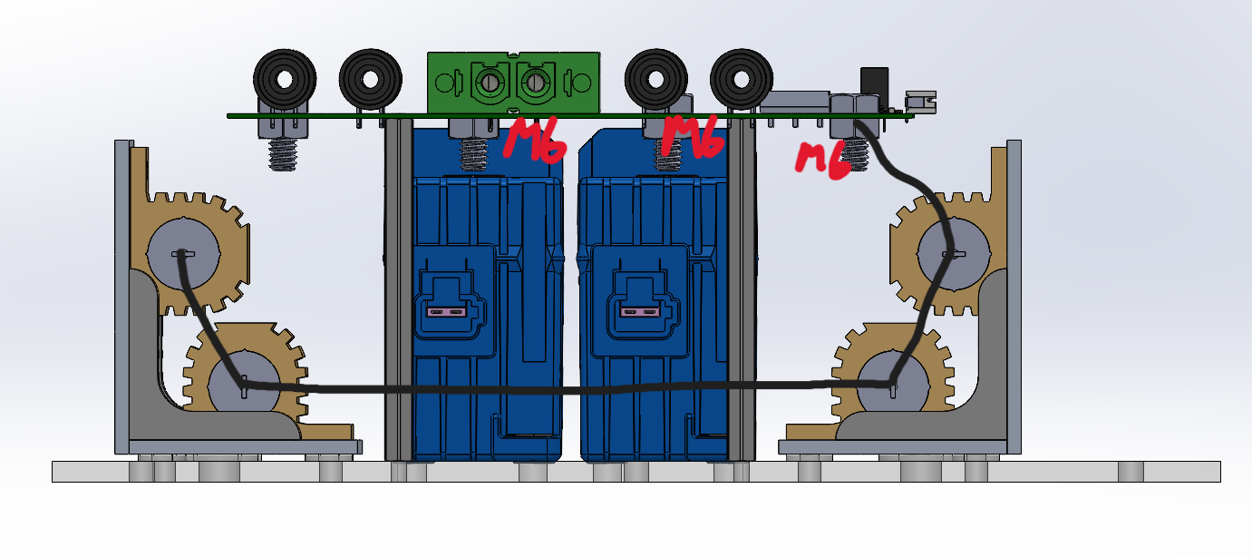
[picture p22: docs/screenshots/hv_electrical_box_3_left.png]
hv-electrical-box-3-left


Attach the contactor connector accessories to the Main Board PCB, then attach the Main Board PCB to the acrylic front panel using the two #4-40 1" standoffs and #4-40 screws. Then, insert the contactor connector accessories into the ports on the side of the contactors. When finished with this step, the box should look something like this (of course, the front panel will not stand on its own like in the picture; you can lay it face-down for now):

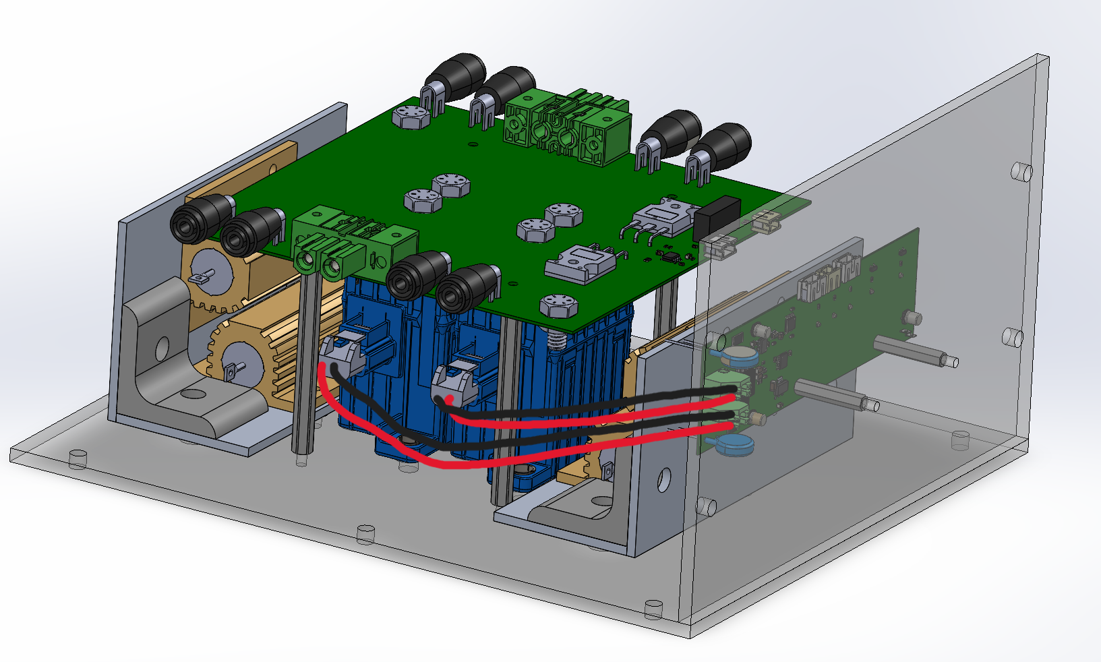
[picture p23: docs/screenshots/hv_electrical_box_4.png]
hv-electrical-box-4


Push the head of the barrel jack output of the 120V-12V AC-DC converter through the large hole in the acrylic back panel and pull it through. Attach it to the Main Board PCB. Now, the box should look something like this (again, the front and back panels will not stand on their own like in the picture; you can lay both of the face-down for now):

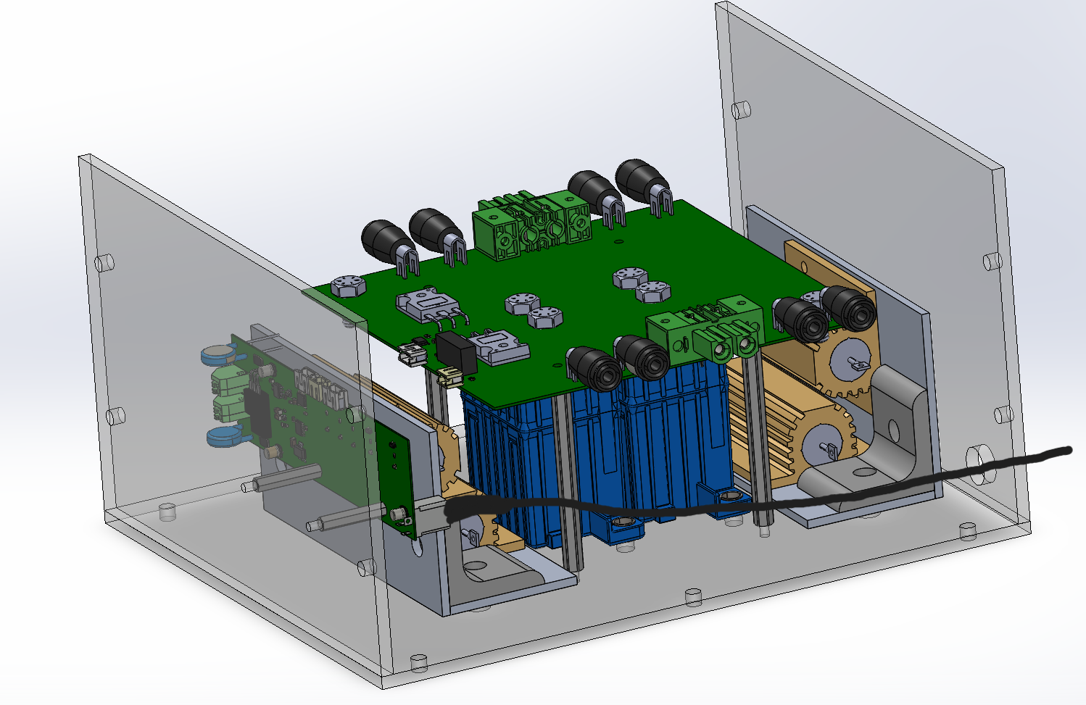
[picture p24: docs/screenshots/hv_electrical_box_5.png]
hv-electrical-box-5


Assemble the two side panels. They are mirror images of each other. Remember the 20 series aluminum beams go on the **outside** of the box! There are no L brackets that hold the aluminum beams together; these aluminum beams simply provide a place for all of the different panels to screw into. Below is an annotated diagram of one side panel. Beam lengths are called out in red. Green circles indicate positions of T nuts for accomodating the bolts which secure the acrylic panel to the beams. Purple circles indicate positions of T nuts for accomodating the bolts which secure various other components to the beams (which will be used in later steps).

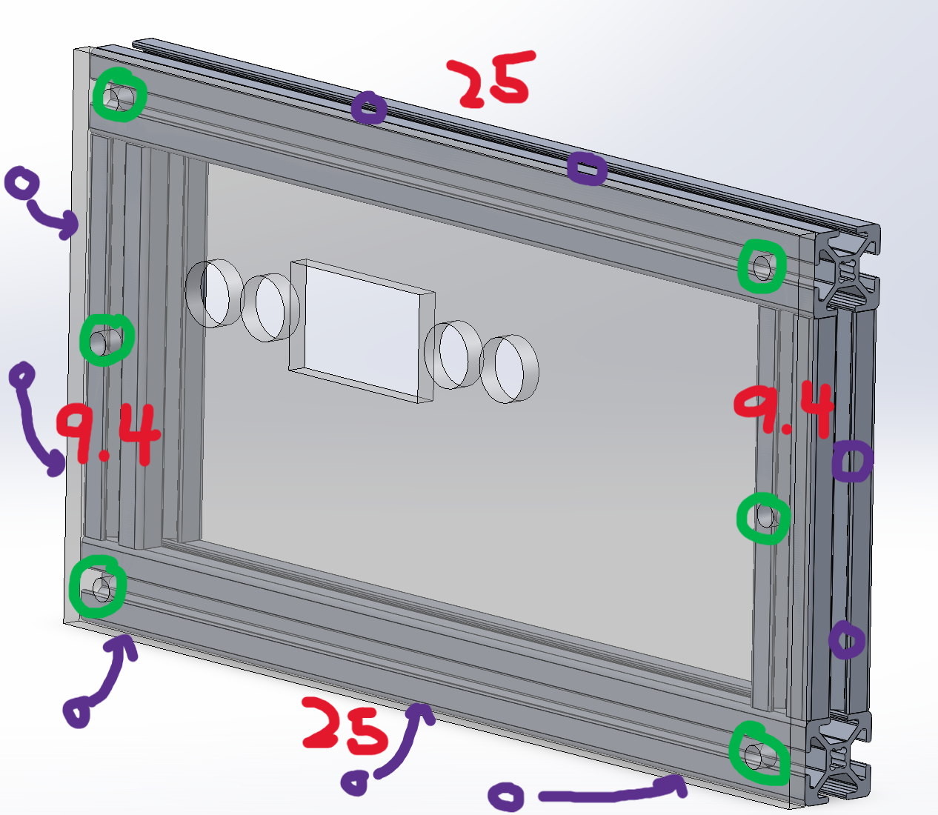
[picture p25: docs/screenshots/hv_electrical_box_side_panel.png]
hv-electrical-box-side-panel


Attach the two side panels to the bottom panel, securing them in place with six screws from the bottom. Then, attach the front and back panels, securing them in place with four screws from the front, and four screws from the back. Below is a diagram showing the screws needed to secure the side panels to the bottom panel (in green, should be done first), and the screws to secure the front and back panels to the beams (in purple, should be done second):

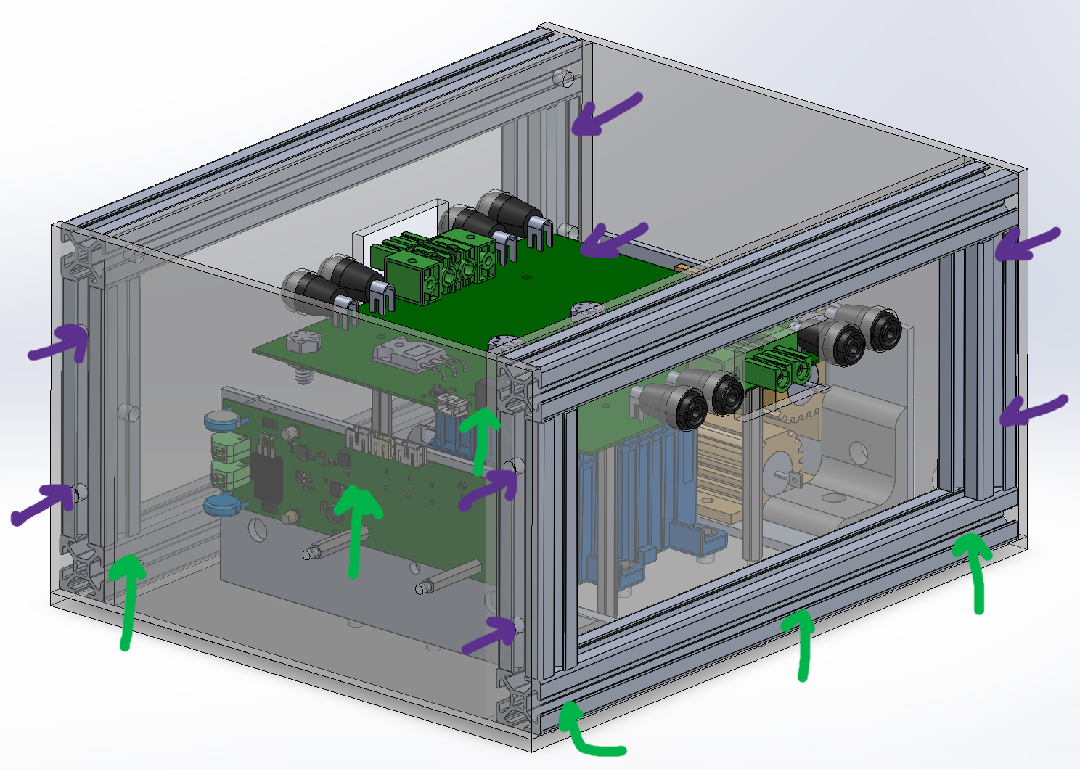
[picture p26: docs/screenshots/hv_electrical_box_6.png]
hv-electrical-box-6


This completes Step 3.

## Step 4: The Auxiliary High Voltage Electrial Box

Assemble the bleeder resistor assembly. Attach the bleeder resistors to the head sink and the heat sink to the bottom panel using #8-32 screws. Ensure that there are nylon spacers between the bottom of the heat sink and the top of the acrylic panel, and between the bottom of the acrylic panel and the #8-32 nut. When completed, the assembly should look like this:

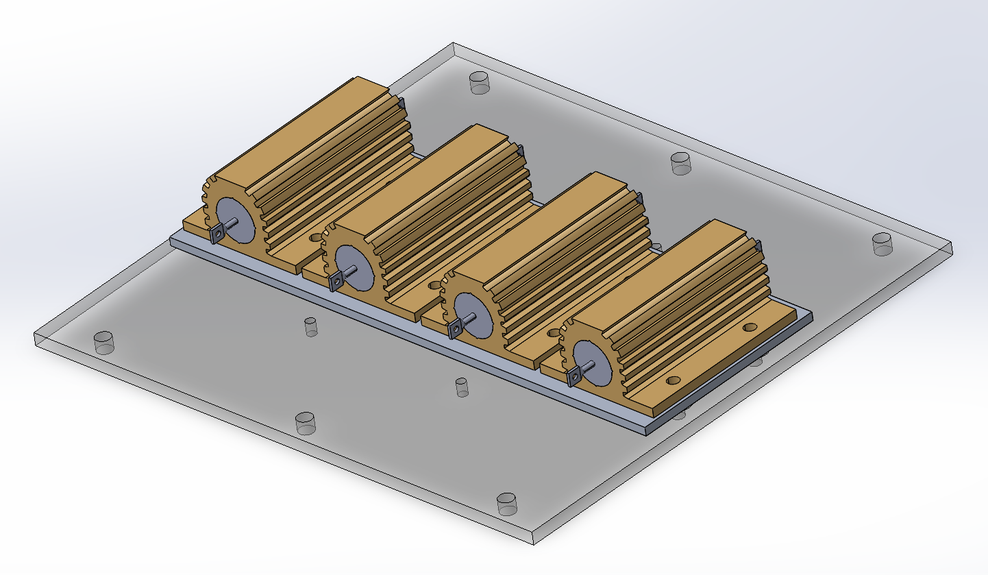
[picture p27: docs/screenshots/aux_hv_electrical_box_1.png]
aux-hv-electrical-box-1


Attach the four #4-40 2" standoffs to the bottom panel using #4-40 screws. When completed, the assembly should look like this:

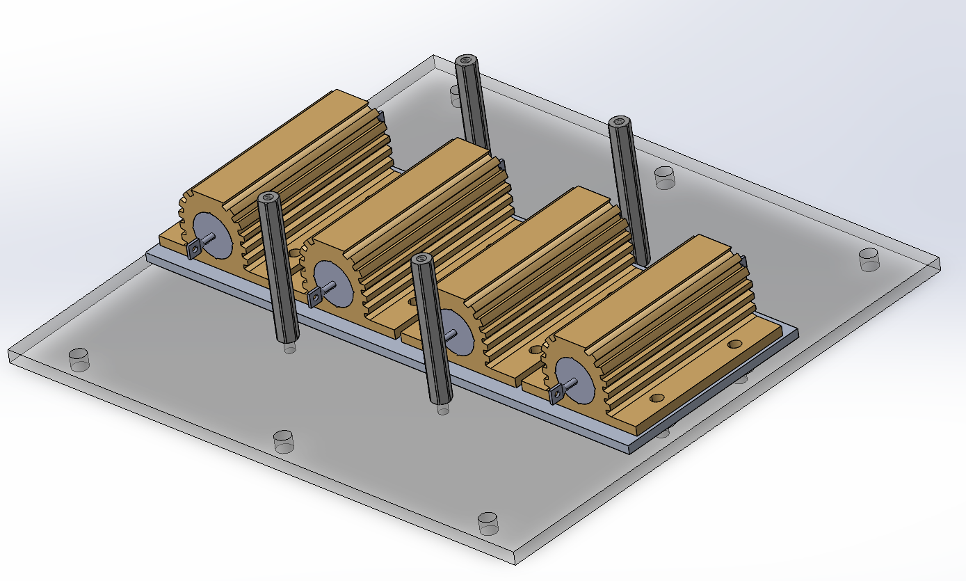
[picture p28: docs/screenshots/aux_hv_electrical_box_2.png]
aux-hv-electrical-box-2


Solder the wires connecting the bleeder resistors together on both sides, and that connect the bleed resistors up to the Aux HV Board. The wire gauge and the method that they are attached to the Aux HV Board is the same as for the HV Board in Step 3. Put the Aux HV Board on top of the standoffs and bolt down the M6 bolts that attach the Aux HV Board to the ring terminal connected to the bleed resistor wires. When finished, the box should look like the pictures below, with wires drawn on as an example:

Right view:
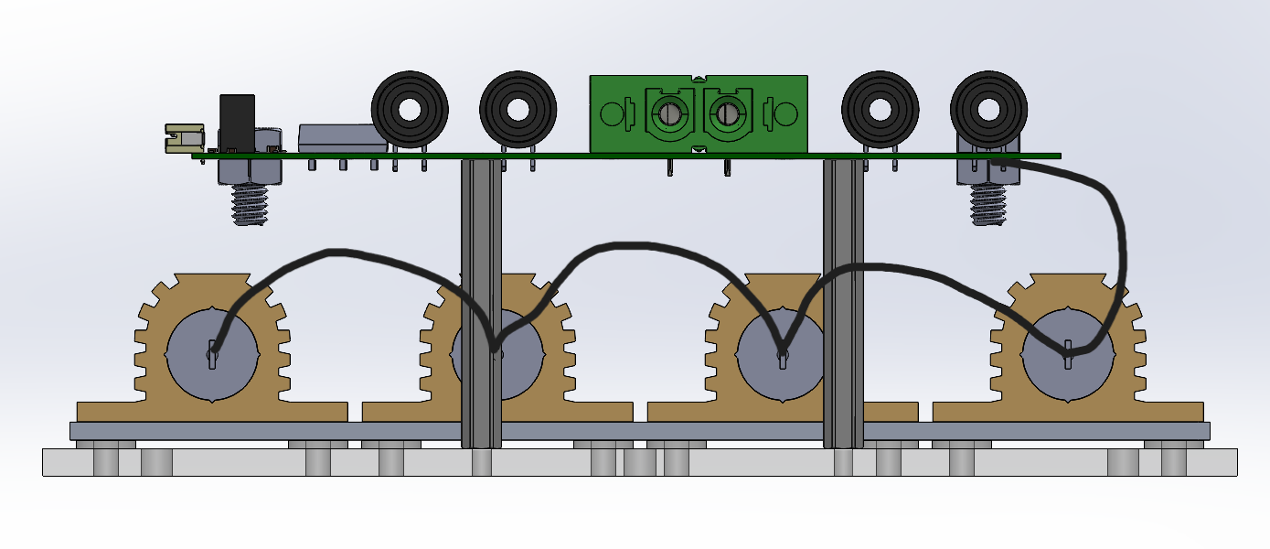
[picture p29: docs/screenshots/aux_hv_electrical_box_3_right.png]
aux-hv-electrical-box-3-right


Left view:
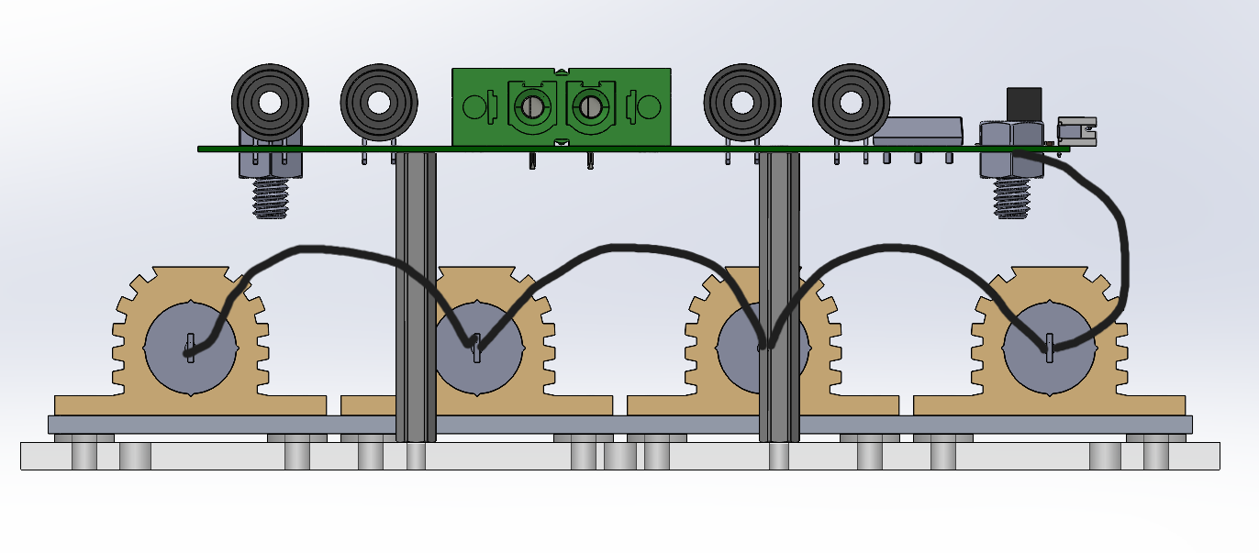
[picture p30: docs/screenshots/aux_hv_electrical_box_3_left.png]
aux-hv-electricral-box-3-left


Assemble the two side panels. They are mirror images of each other. Remember the 20 series aluminum beams go on the **outside** of the box! There are no L brackets that hold the aluminum beams together; these aluminum beams simply provide a place for all of the different panels to screw into. Below is an annotated diagram of one side panel. Beam lengths are called out in red. Green circles indicate positions of T nuts for accomodating the bolts which secure the acrylic panel to the beams. Purple circles indicate positions of T nuts for accomodating the bolts which secure various other components to the beams (which will be used in later steps).

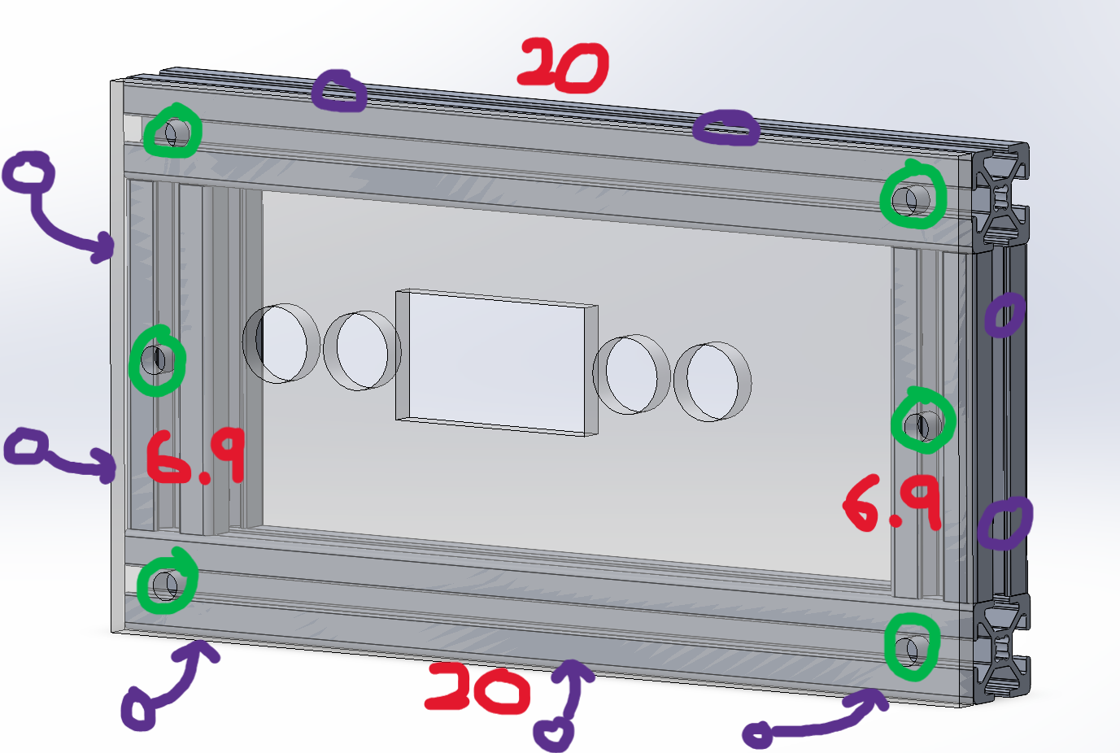
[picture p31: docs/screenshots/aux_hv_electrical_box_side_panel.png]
aux-hv-electrical-box-side-panel


Attach the two side panels to the bottom panel, securing them in place with six screws from the bottom. Then, attach the front and back panels, securing them in place with four screws from the front, and four screws from the back. Below is a diagram showing the screws needed to secure the side panels to the bottom panel (in green, should be done first), and the screws to secure the front and back panels to the beams (in purple, should be done second):

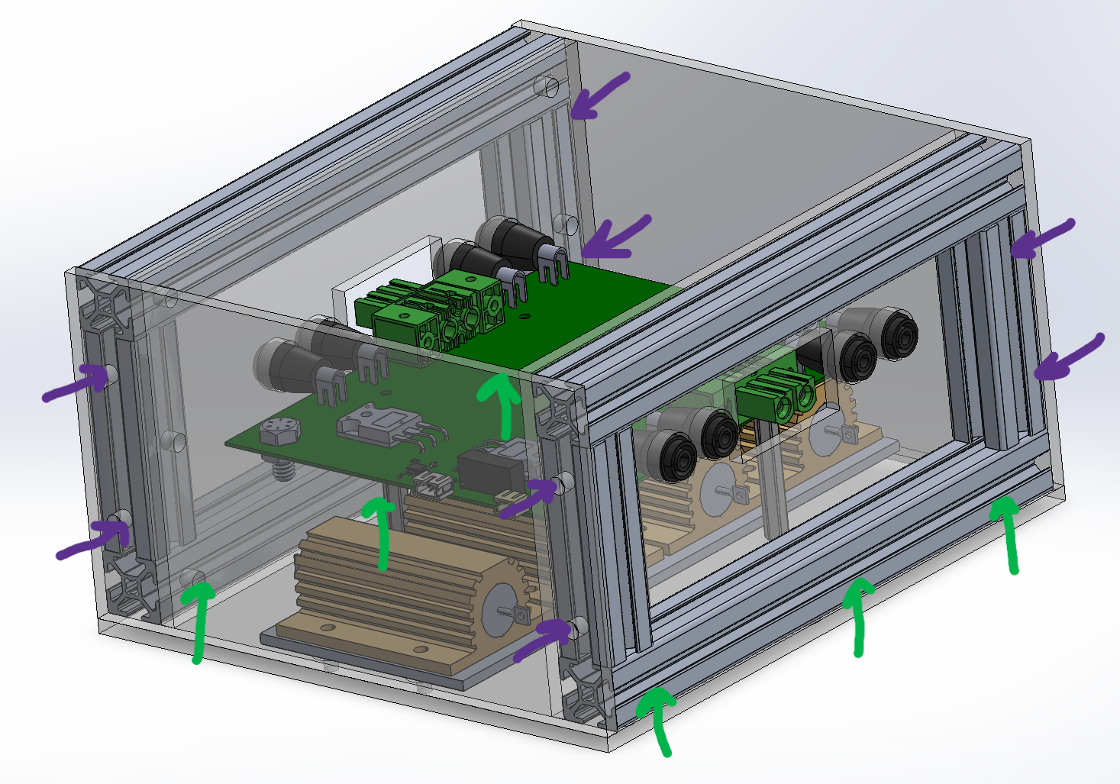
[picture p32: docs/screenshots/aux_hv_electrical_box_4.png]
aux-hv-electrical-box-4


This completes Step 4.

## Step 5: Connecting the Electrical Box(es) to the Cover

Attach the boxes to the beam on the cover using the gusseted L brackets without guides from 8020.net. Below is an annotated diagram showing where the L brackets go:

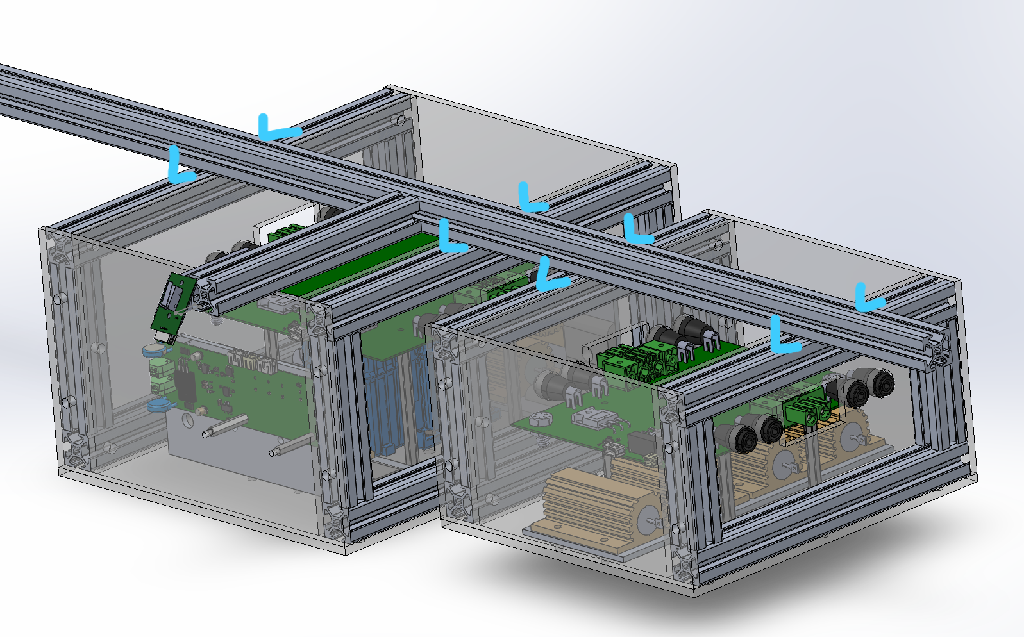
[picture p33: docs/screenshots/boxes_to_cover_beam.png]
boxes-to-beam-diagram


This completes Step 5. The finished cover can now be mounted to the desk, and a gate latch fitted in a suitable place on the top shelf.

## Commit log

2024-08-28 Added all mechanical design files with updated references and names
    [2020_100.SLDPRT, 2020_15.SLDPRT, 2020_20.SLDPRT, 2020_25-4.SLDPRT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]
2024-08-28 Renamed a few more files and added docs folder
    [aux_board_head_sink_resistors.SLDPRT, aux_hv_board_bleeder_resistor_assembly.SLDASM, aux_hv_box_heat_sink.SLDPRT, aux_hv_pcb_assembly.SLDASM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]
2024-08-29 Added dxf and stl files to separate production folder
    [aux_board_head_sink_resistors.DXF, aux_hv_board_box_bottom_panel.DXF, aux_hv_board_box_front_back_panel.DXF, aux_hv_board_box_side_panel.DXF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]
2024-08-29 Added .gitignore file, added Altium files for Button Board and gerbers in separate production/gerbers folder
    [Button_Board.PrjPcb, Button_Board.SchDoc, Button_Board_PCB.PcbDoc]
2024-08-29 Added Main Board Altium design files and gerbers
    [Main_Board.PrjPcb, Main_Board.SchDoc, Main_Board_PCB.PcbDoc]
2024-08-29 Added HV Board Altium design files and gerbers
    [HV_Board.PrjPcb, HV_Board.SchDoc, HV_Board_PCB.PcbDoc]
2024-08-29 Added Aux HV Board Altium design files and gerbers
    [Aux_HV_Board.PrjPcb, Aux_HV_Board.SchDoc, Aux_HV_Board_PCB.PcbDoc]
2024-08-29 Fixed full model cover movement by adding a mate
    [cover_hinge_attachment.SLDASM, hinge_assembly.sldasm]
2024-08-30 Added Main Board BOM
2024-08-30 Finished BOMs for PCBs
2024-08-30 Filled out a few more BOMs
    [heat_sink_bottom_resistor.DXF, heat_sink_side_resistor.DXF]
2024-08-30 Finished adding 8020 BOM
    [cover_hinge_attachment.SLDASM, hinge_assembly.sldasm]
2024-09-02 Added assembly instructions and screenshots
    [aux_hv_pcb_assembly.SLDASM, cover_hinge_attachment.SLDASM, hinge_assembly.sldasm]
2024-09-02 Fixed links in assembly instructions
2024-09-02 Edited assembly instructions and fixed bugs
2024-09-02 Filled out Altium BomDoc for Aux HV Board, HV Board, and Main Board
